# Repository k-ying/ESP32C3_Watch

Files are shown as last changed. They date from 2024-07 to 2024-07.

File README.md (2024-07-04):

# ESP32C3Watch
## 1. Brief/简介
The smartwatch made based on ESP32-C3(RISC-V MCU), which has heart rate, oximetry, temperature, fall detection and IOT Function. 

> 基于 ESP32-C3的智能手表（RISC-V MCU），具有心率、血氧饱和度、温度、跌倒检测和物联网功能。

The project stems from My Graduation Project in 2022, Since the time for secrecy has ended, I can open source its design and code.The project may be very old, some components and functions can not be used directly, need to be adjusted according to the latest library, please be aware of.

> 该项目源于2022年的毕业设计，因为已满足时间，所以开源其设计与代码。该项目可能比较旧了，有些组件和函数不能直接使用，需要根据最新的库进行调整，请悉知。

Here are the folder descriptions:
1. HardWare: used to store hardware related, circuit design and PCB design, using KiCAD for the design of the project; also contains 3D models and peripherals DataSheet.
2. Software: used to store the programme code of CMU master control, this project uses ESP-IDF (LVGL library) of VScode environment to build the project, the version may be very old.
3. Article: thesis and reference materials.
4. images: README.md needed images.

> 以下是文件夹说明：
> 1. HardWare：用于存放硬件相关，电路设计及PCB设计，使用KiCAD进行设计的工程；还包含3D模型及外设DataSheet。
> 2. Software：用于存放CMU主控的程序代码，该项目使用VScode环境的ESP-IDF(LVGL库)进行工程建立，版本可能很旧了。
> 3. Article：论文及参考资料。
> 4. images：README.md 需要的图片。

## 2. Architecture/架构：
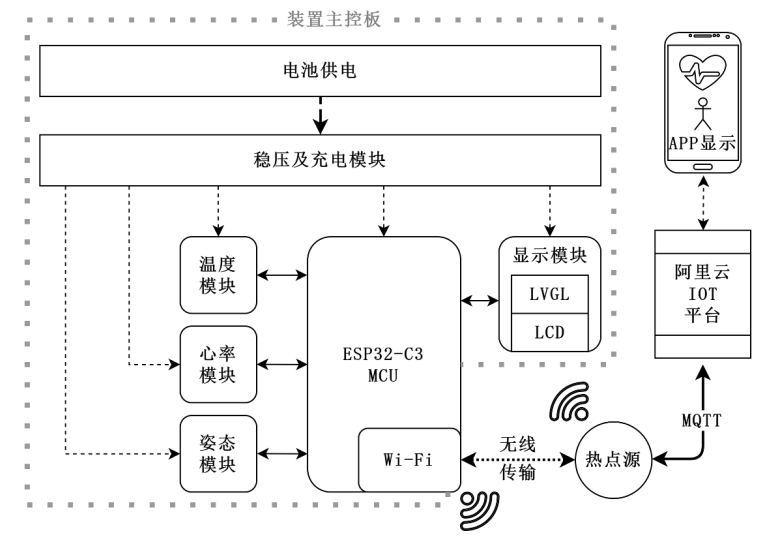
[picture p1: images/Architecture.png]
Architecture


In view of foreign chip design enterprises may take the technology monopoly, coupled with the COVID-19 has made people pay more attention to a healthy life. This topic designed a wearable human health monitoring device based on RISC-V architecture MCU, which can detect the wearer's heart rate, blood oxygen saturation, skin surface temperature, and exercise status in real-time. After scheme comparison, the ESP32-C3 series of Espressif Systems CO., LTD. was selected as the master chip. The MAX30102 sensor was used to obtain photoplethysmogram(PPG) signals, which can calculate heart rate and blood oxygen saturation(SpO2) data. MAX30205 was used to obtain real-time temperature, and MPU-6050 Inertial measurement unit(IMU) was used to obtain motion state data, so as to realize the functions of sedentary and falling reminder.

A GUI interface based on LVGL allows users to interact with the device and view data, ifconnected to a Wi-Fi hotspot, it will upload data to the AliCloud IOT server via MQTT. Through the AliCloud data visualization platform, users can view historical data and fall alarm information by using the supporting APP.

After finishing the design, the device defects were found and optimized through various 
functional tests. Finally, good stability of the device and accuracy of data was realized.

> 鉴于国外芯片设计企业可能采取的技术垄断，加之疫情让人们对健康生活更加重视，本课题设计了一款基于 RISC-V 架构 MCU 的穿戴式人体健康监测装置，可实时检测佩戴者的心率和血氧饱和度、皮肤表面温度以及运动状态等健康参数。经过方案比对，最终选择乐鑫科技的 ESP32-C3 系列作为主控芯片，使用 MAX30102 传感器获取光电容积脉搏波（PPG）并计算心率、血氧饱和度(SpO2)数据，通过 MAX30205 获取实时温度、MPU-6050 惯性测量单元(IMU)获取运动状态数据，从而实现久坐、跌倒提醒等功能。

> 用户可通过基于 LVGL 设计的 GUI 界面进行人机交互、数据查看，还可将装置连接至 Wi-Fi 热点，数据会通过 MQTT 协议上传至阿里云 IOT 服务器。借由阿里数据可视化平台，用户端可使用配套 APP 查看历史数据、跌倒警报信息等。

> 装置设计完成后，通过各项功能测试，发现存在设计缺陷并进行了改正及优化，最终实现了装置的稳定与数据的准确可靠。

## 3. Schematic/原理图
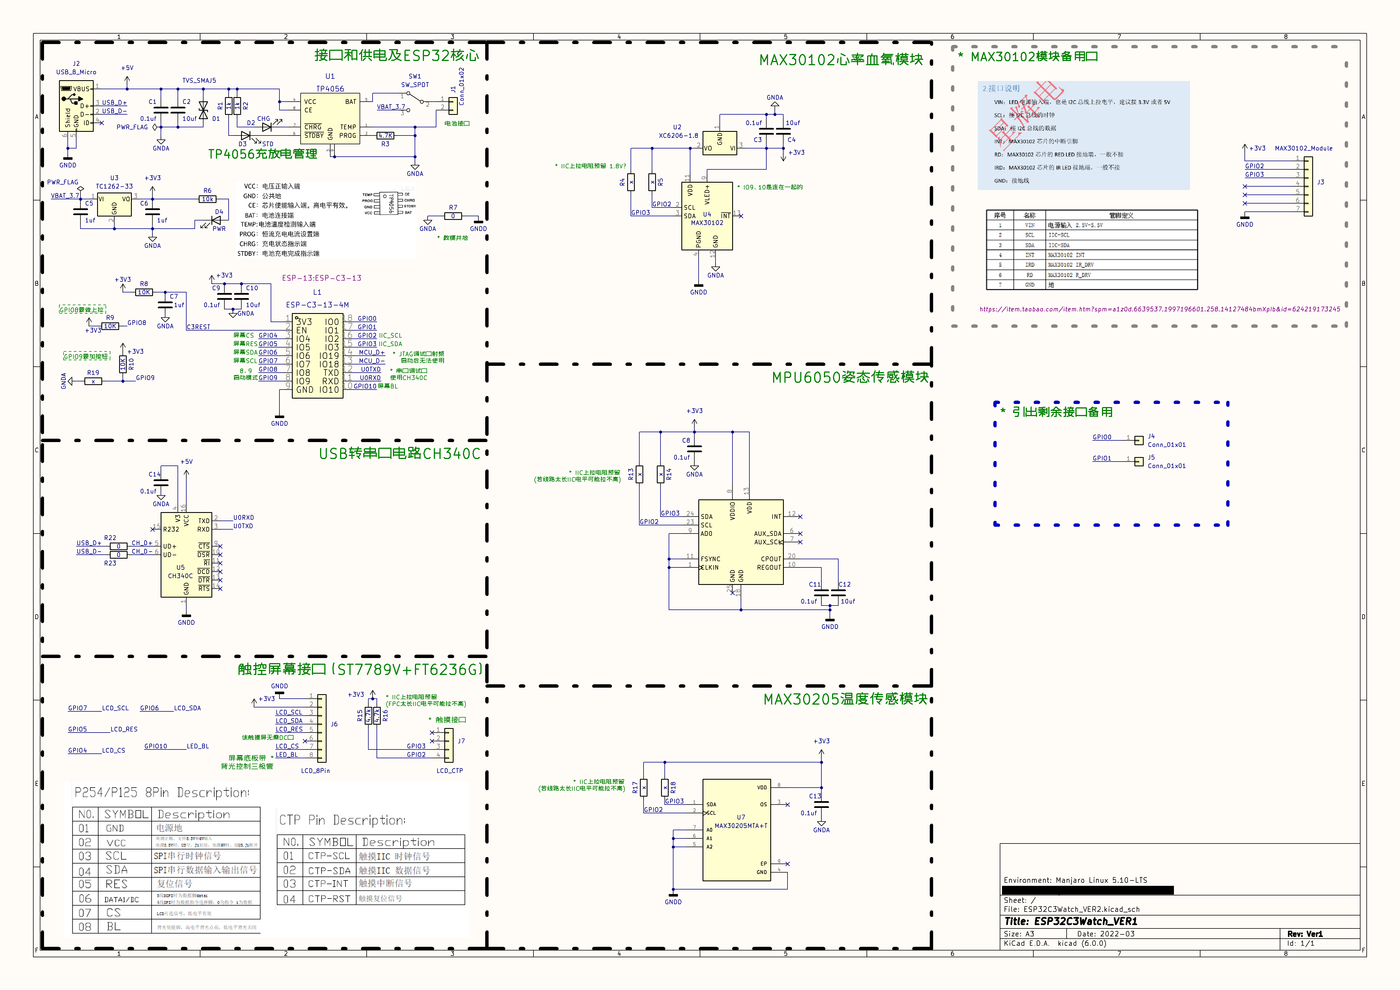
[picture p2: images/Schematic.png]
Schematic


For a detailed description, please see the Article/ESP32C3Watch_CN.pdf

> 详细的介绍请见文件 Article/ESP32C3Watch_CN.pdf

## 4. PCB

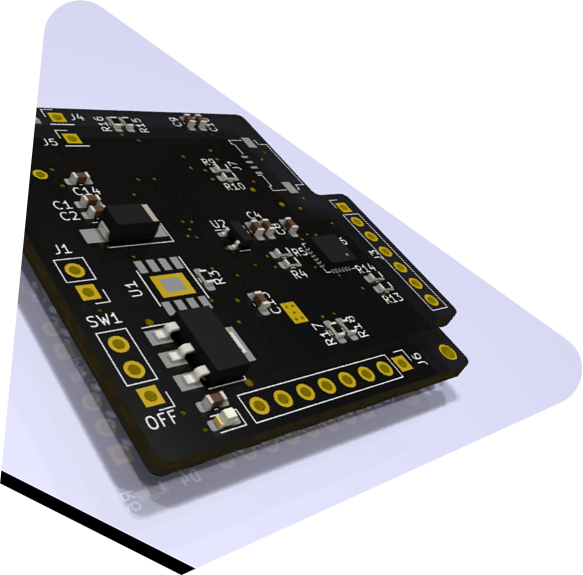
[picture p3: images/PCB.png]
PCB


The PCB is just used as a reference, it can actually be made better and smaller. For a detailed description, please see the Article/ESP32C3Watch_CN.pdf

> PCB只是作为一个参考，实际上它可以做得更好、更小巧。详细的介绍请见文件 Article/ESP32C3Watch_CN.pdf

## 5. Function/功能

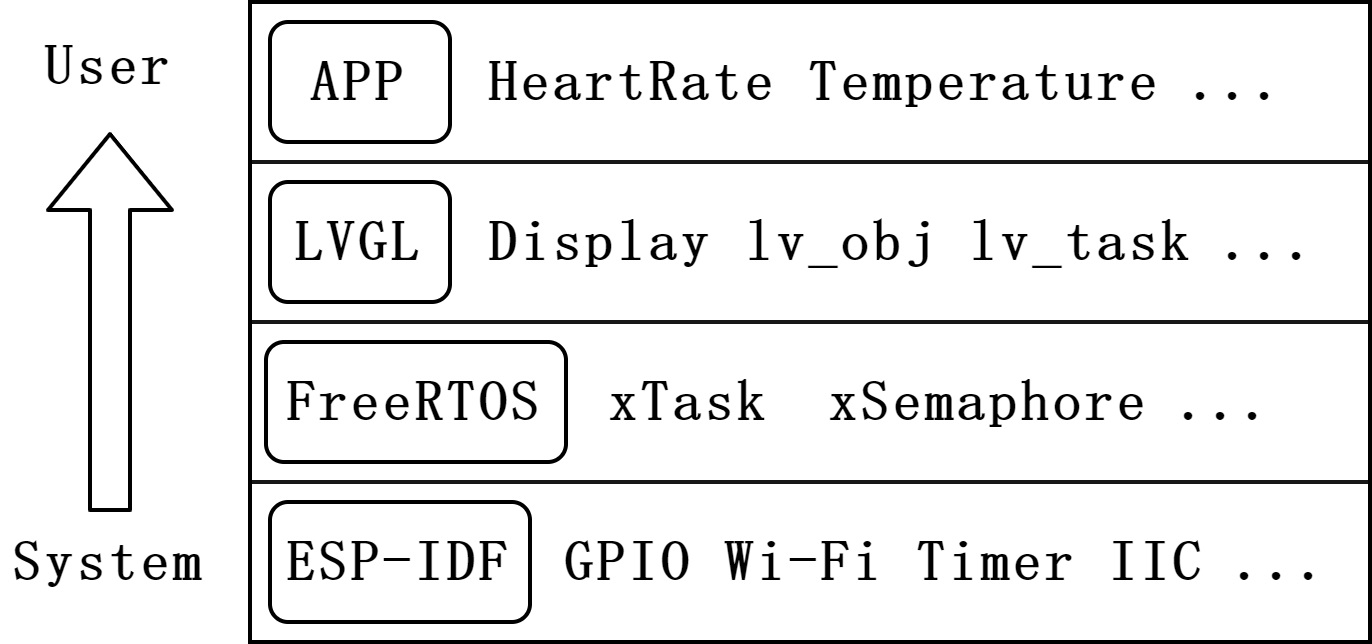
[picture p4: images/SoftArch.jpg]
SoftArch


For a detailed description, please see the Article/ESP32C3Watch_CN.pdf

> 详细的介绍请见文件 Article/ESP32C3Watch_CN.pdf

## 6. Display results/结果展示

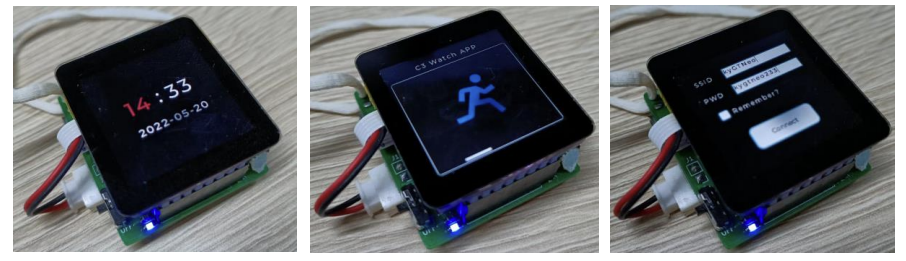
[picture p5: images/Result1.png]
Result1


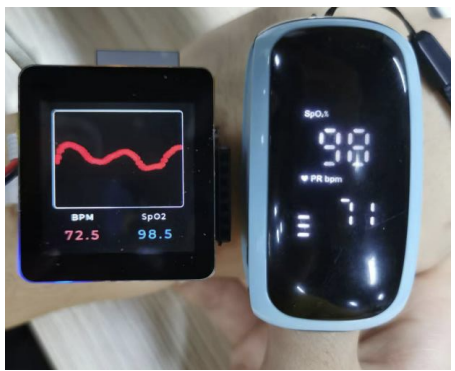
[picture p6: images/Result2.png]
Result2


For a detailed description, please see the Article/ESP32C3Watch_CN.pdf

> 详细的介绍请见文件 Article/ESP32C3Watch_CN.pdf

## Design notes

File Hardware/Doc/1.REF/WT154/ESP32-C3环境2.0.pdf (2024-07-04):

ESP32-C3 环境准备

1. Windows 环境搭建
a) 获取 ESP-IDFG
Windows 去官方网站下载一个 ESP-IDF 工具安装器 https://dl.espressif.com/dl/esp-idf/?idf=4.4 我这里使用的是离线安装器

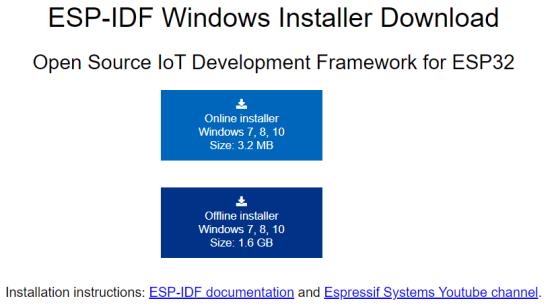
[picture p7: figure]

b) 安装

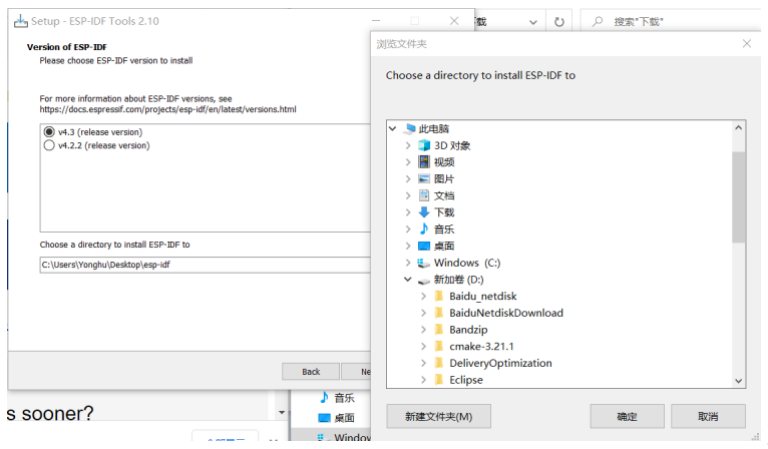
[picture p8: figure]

建议在 D 盘创建一个文件

夹去保存该 ESP-IDF ,因为后面需要把工程放在同一个目录下

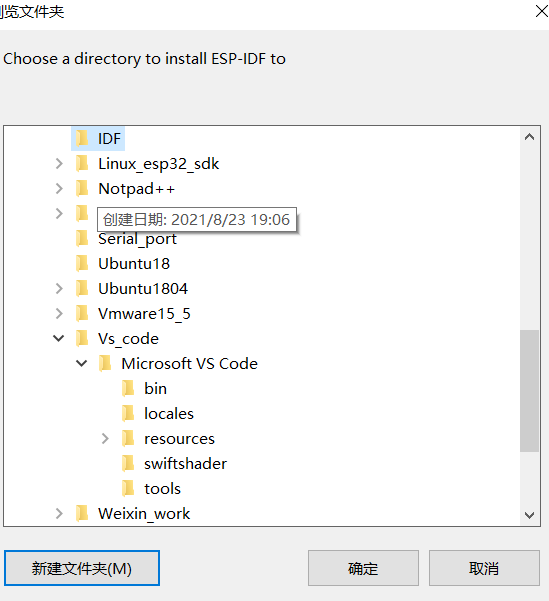
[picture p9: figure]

建立一个 IDF 文件夹去保存该 esp-idf 直接一直下一步到安装

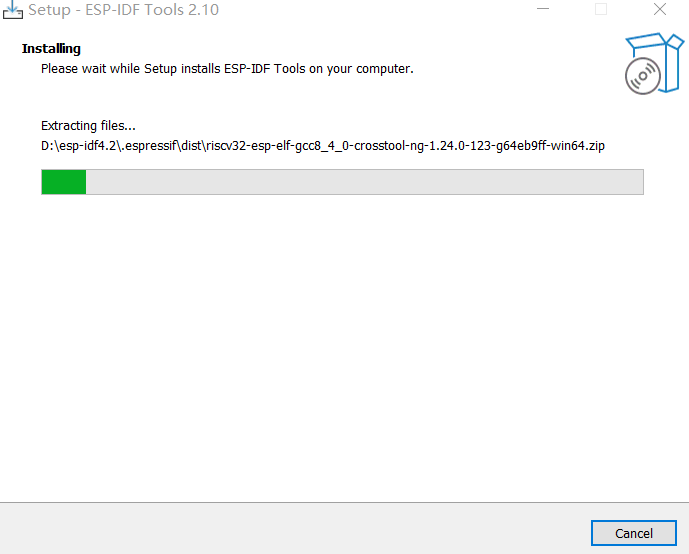
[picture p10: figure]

安装完成后会在桌面生成

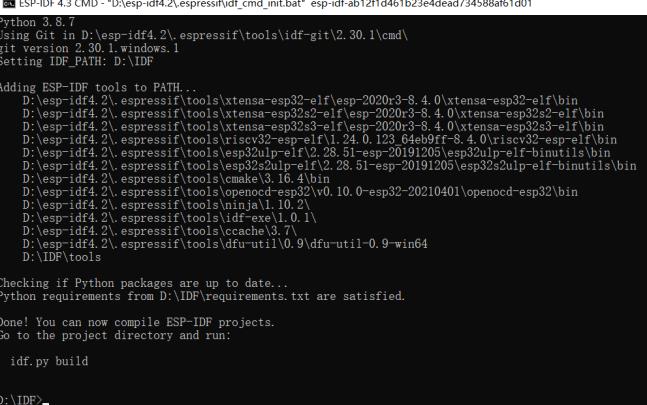
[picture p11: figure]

可以以管理身份运行( 但是不推荐), 如图已经可以使用 idf.py build 这样环境搭建完成,下面开始编译工程
2. 工程
a) 拷贝工程

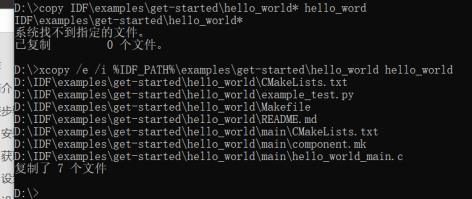
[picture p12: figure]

将 hello_word 复制到 d 盘下
xcopy /e /i %IDF_PATH%\examples\get-started\hello_world hello_world 这里安装没安装到 IDF 子目录下,所以选择直接在 d 盘选择一个文件夹作为工程目录 使用 dir 指令 查看当前所有文件

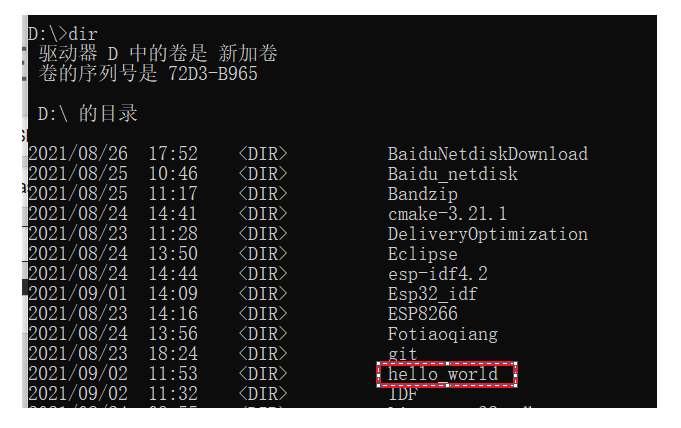
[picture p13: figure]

这个便是已经复制好的工程文件了
b) 设备连接

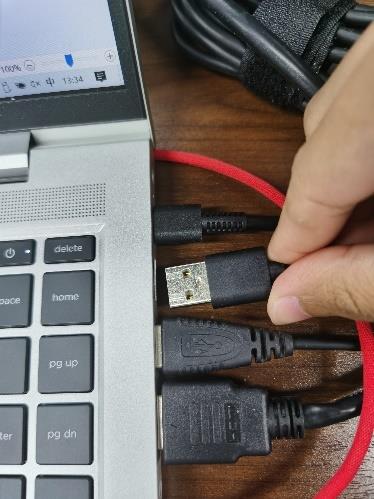
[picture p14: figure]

c) 设置目标芯片 :

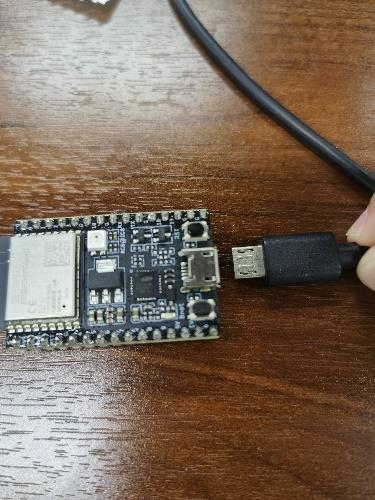
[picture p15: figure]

idf.py set-target esp32c3 设置目标芯片

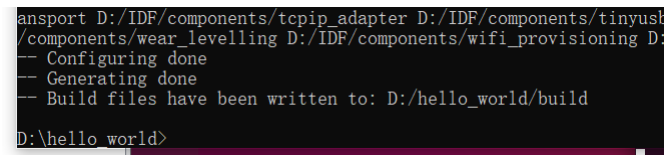
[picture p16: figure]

idf.py menuconfig 打开工程配置主窗口命令

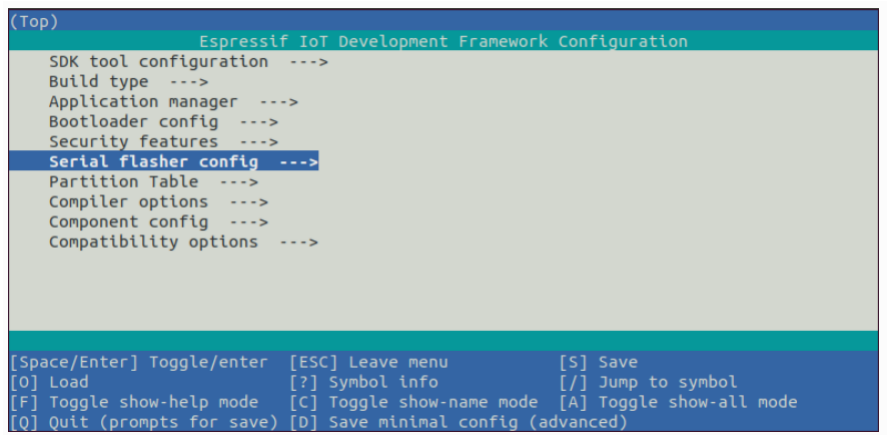
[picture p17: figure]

d) 编译工程
进入到已经克隆的文件 hello_world 编译命令 : idf.py build

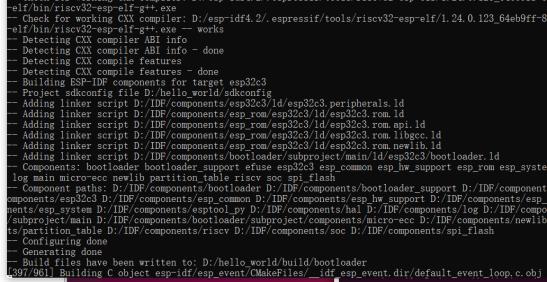
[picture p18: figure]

e) | 烧入到设备 idf.py -p port [ -b BAUD] | flash
-p port 表示需要指定的端口号 -b BAUD 可以不用写指的是波特率不写默认烧入波特率为 :
| 460800
f) 环境 打开设备管理器 找到
| 按下 windows 按键/鼠标单击左小角

键盘输入设备管理器

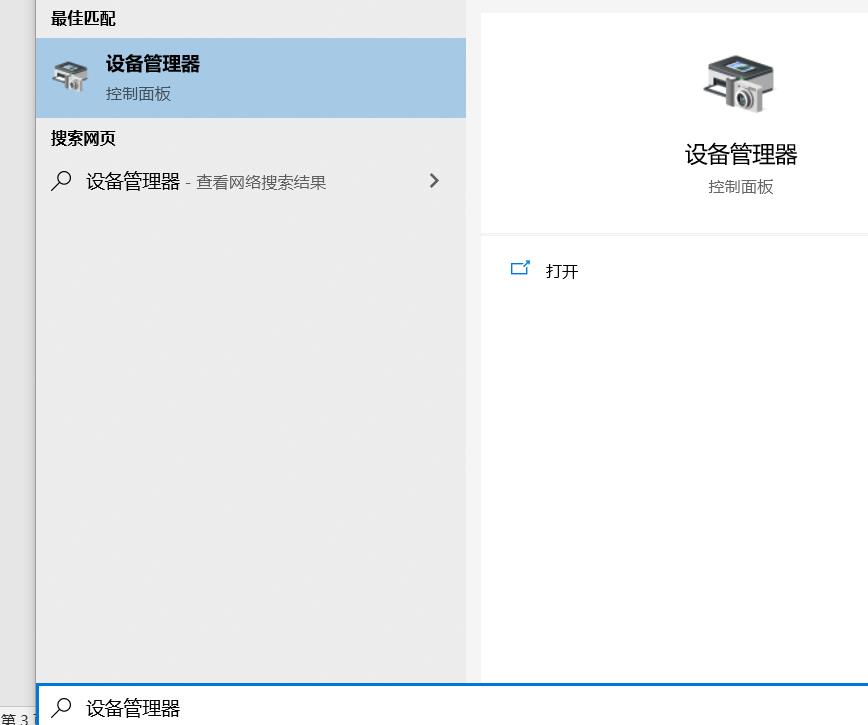
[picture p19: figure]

找到 COM 和 LPT 选项

当 COM 口未连接设备不会有该选项
idf.py -p (PORT) monitor
这个 PORT 即端口号, 如上则是 COM3 命令 : idf.py -p COM3 monitor 也可以使用软件 : 串口调试工具

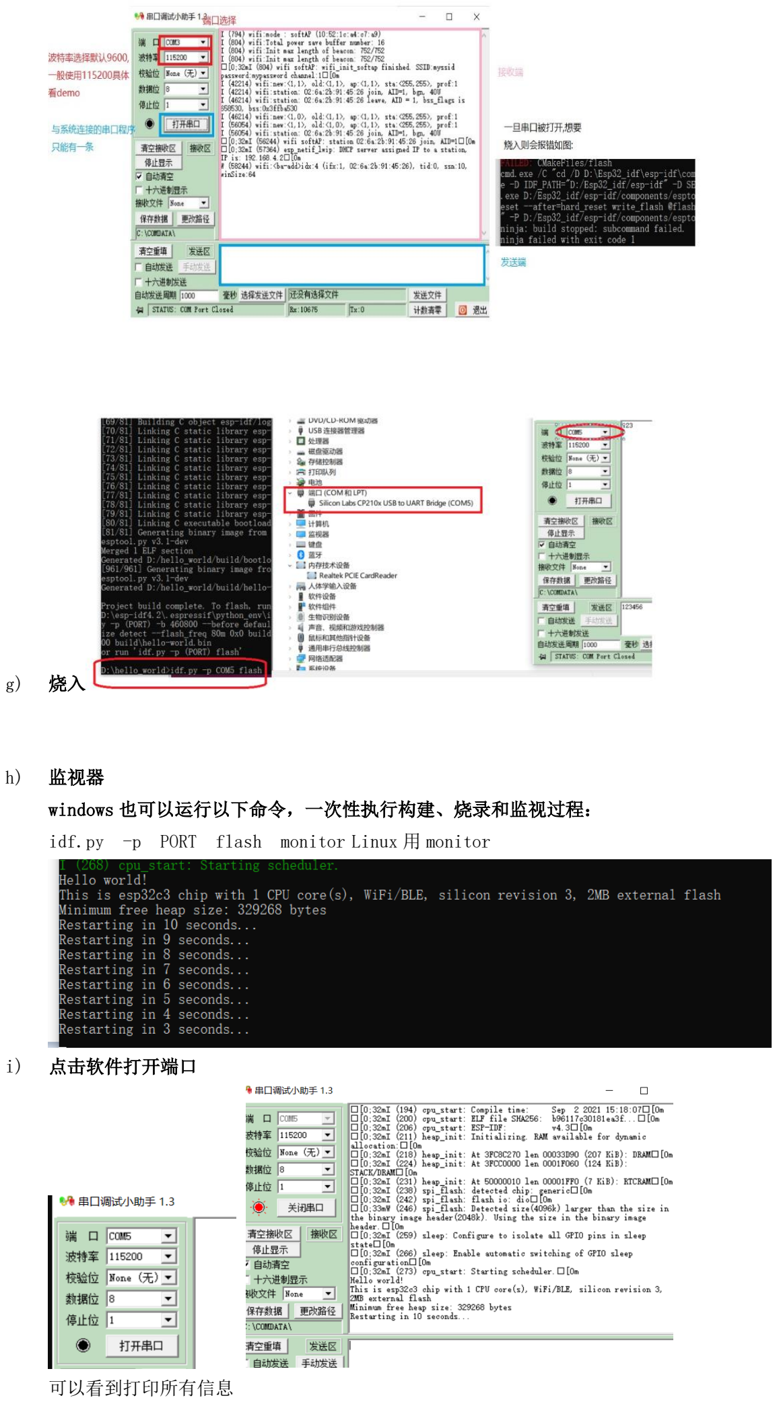
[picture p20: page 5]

g) 烧入
h) 监视器
windows 也可以运行以下命令，一次性执行构建、烧录和监视过程： idf.py -p PORT flash monitor Linux 用 monitor
i) 点击软件打开端口

可以看到打印所有信息

### Ubuntu 下的环境安装

1. 下载 cmake 及 python3 环境 和 ninja-build git
sudo apt-get install git wget flex bison gperf python3 python3-pip python3-setuptools cmake ninja-build ccache libffi-dev libssl-dev dfu-util libusb-1.0-0
编译的软件包

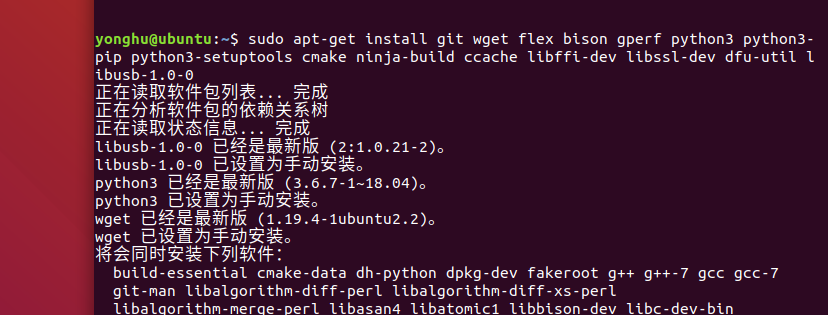
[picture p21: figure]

键入 Y

我们装好了工具, 现在安装 esp-idf 先 cd 到你想安装到的路径我这里选择桌面

2. 在当前路径下创建文件夹 esp 这样可以看见桌面生成了一个文件夹 cd ./esp 转到刚刚创建的文件夹
git clone --recursive https://github.com/espressif/esp-idf.git 克隆文件到当面路径下,也就是刚刚创建的文件夹 esp

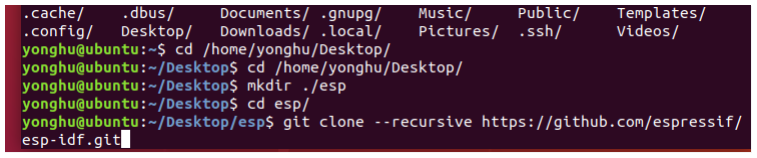
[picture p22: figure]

3. Linux 则需要 先 cd ~/esp/esp-idf 即刚刚下载的路径 这里的 ~ 表示 家目录 /home/yonghu
然后 : ./install.sh esp32c3

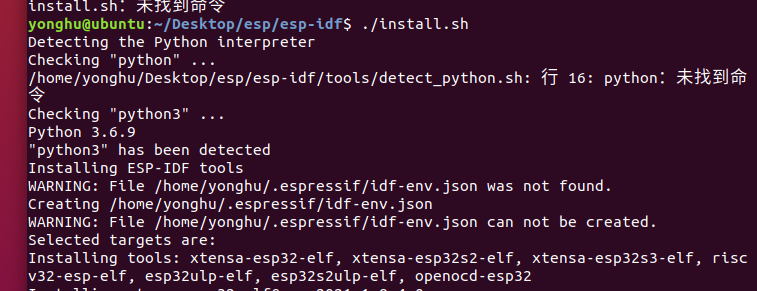
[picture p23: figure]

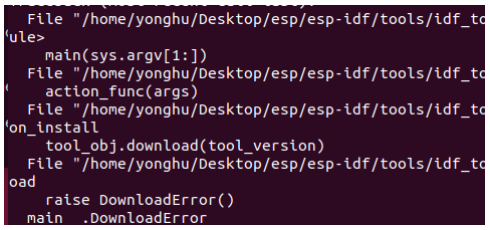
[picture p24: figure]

报错解决办法
输入 git submodule update --init --recursive 更新 需要多次尝试直到完全克隆

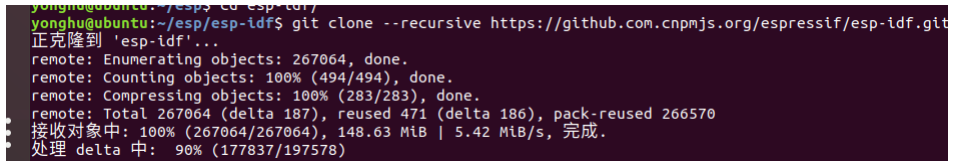
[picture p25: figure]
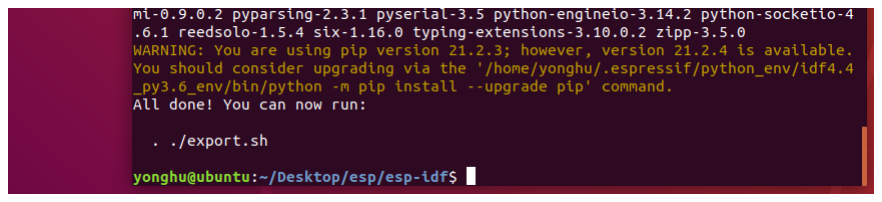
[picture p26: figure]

可能遇见找不到文件
解决办法 : find /usr/include -name "io.h"

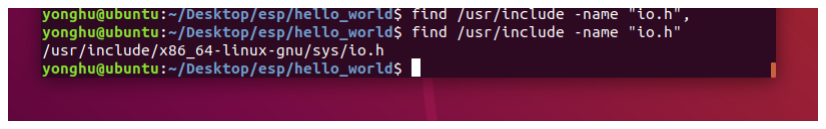
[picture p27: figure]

可以看到 sys 目录下有
/usr/include 下没有，但是在/usr/include/sys 下有，我把 io.h 复制到了/usr/include 下，就行了 由于上面出错可能导致该命令未生效
接着 :. ./export.sh esp32c3 ( esp32c3 打不打无所谓)
4. 写入环境
. $HOME/esp/esp-idf/export.sh
此外，如果您希望在当下命令提示符窗口使用 ESP-IDF，请使用下方代码： 复制并粘贴以下命令到 shell 配置文件中（.profile， .bashrc， .zprofile 等)
alias get_idf='. $HOME/esp/esp-idf/export.sh'
通过重启终端窗口或运行 source [path to profile]，如 source ~/.bashrc 来刷新配置文件。
5. 拷贝目录
cp ./esp-idf/examples/get-started/hello_world/ ./ -r

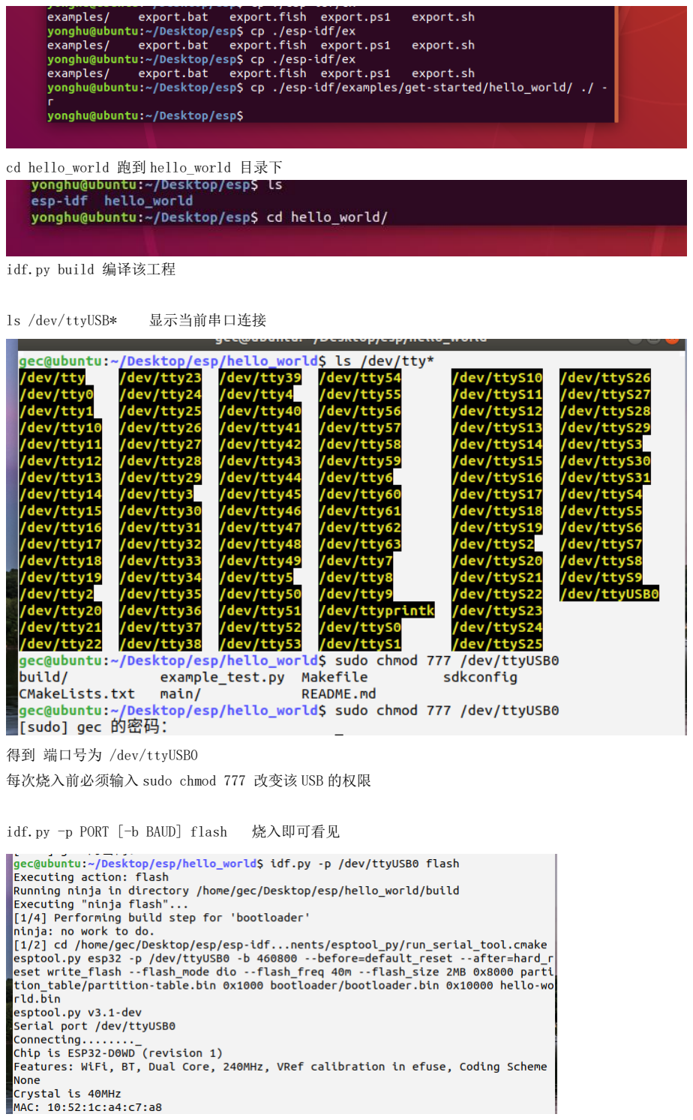
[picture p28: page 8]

cd hello_world 跑到 hello_world 目录下

idf.py build 编译该工程

ls /dev/ttyUSB* 显示当前串口连接

得到 端口号为 /dev/ttyUSB0
每次烧入前必须输入 sudo chmod 777 改变该 USB 的权限

idf.py -p PORT [-b BAUD] flash 烧入即可看见

6. 观察串口打印信息
idf.py -p (PORT) monitor
这个 PORT 即端口号, 如上则是 /dev/ttyUSB0 命令 : idf.py -p /dev/ttyUSB0 monitor

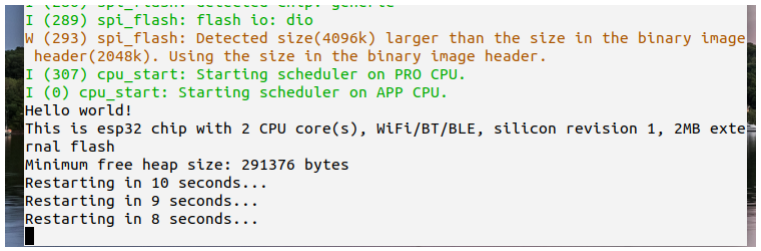
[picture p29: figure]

就可以看见所有打印信息

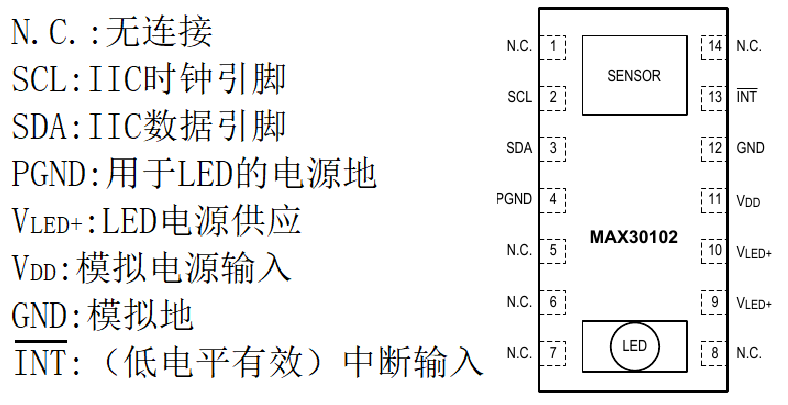
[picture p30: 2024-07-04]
Hardware/Doc/2.DATASHEET/max30102.png

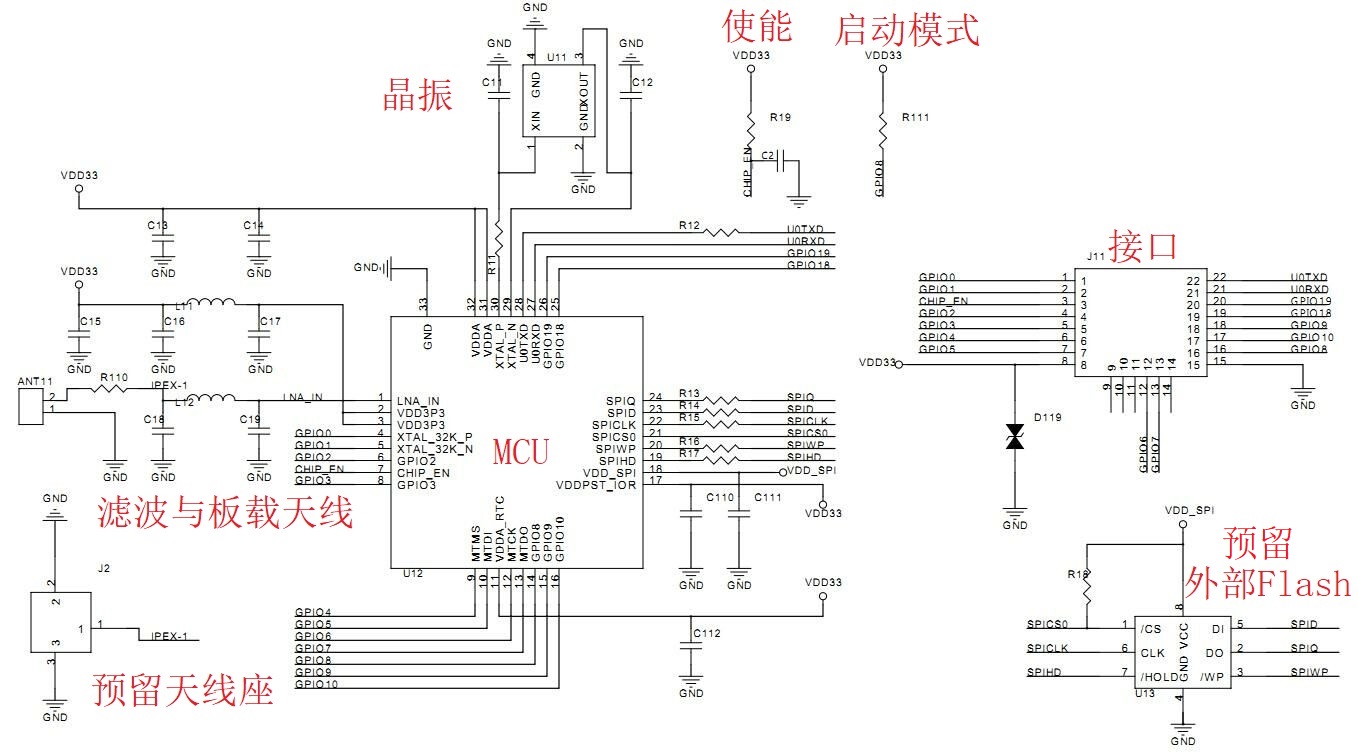
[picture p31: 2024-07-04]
Hardware/Doc/1.REF/esp-c3-13_specification-00000010.jpg

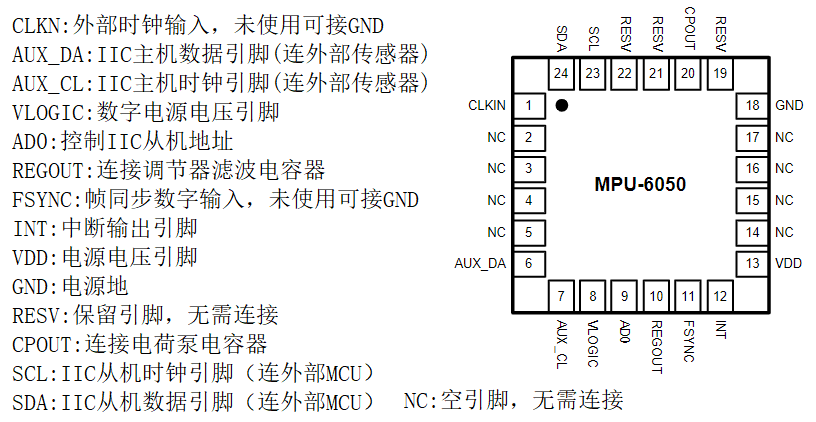
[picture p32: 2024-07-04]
Hardware/Doc/2.DATASHEET/mpu6050.png

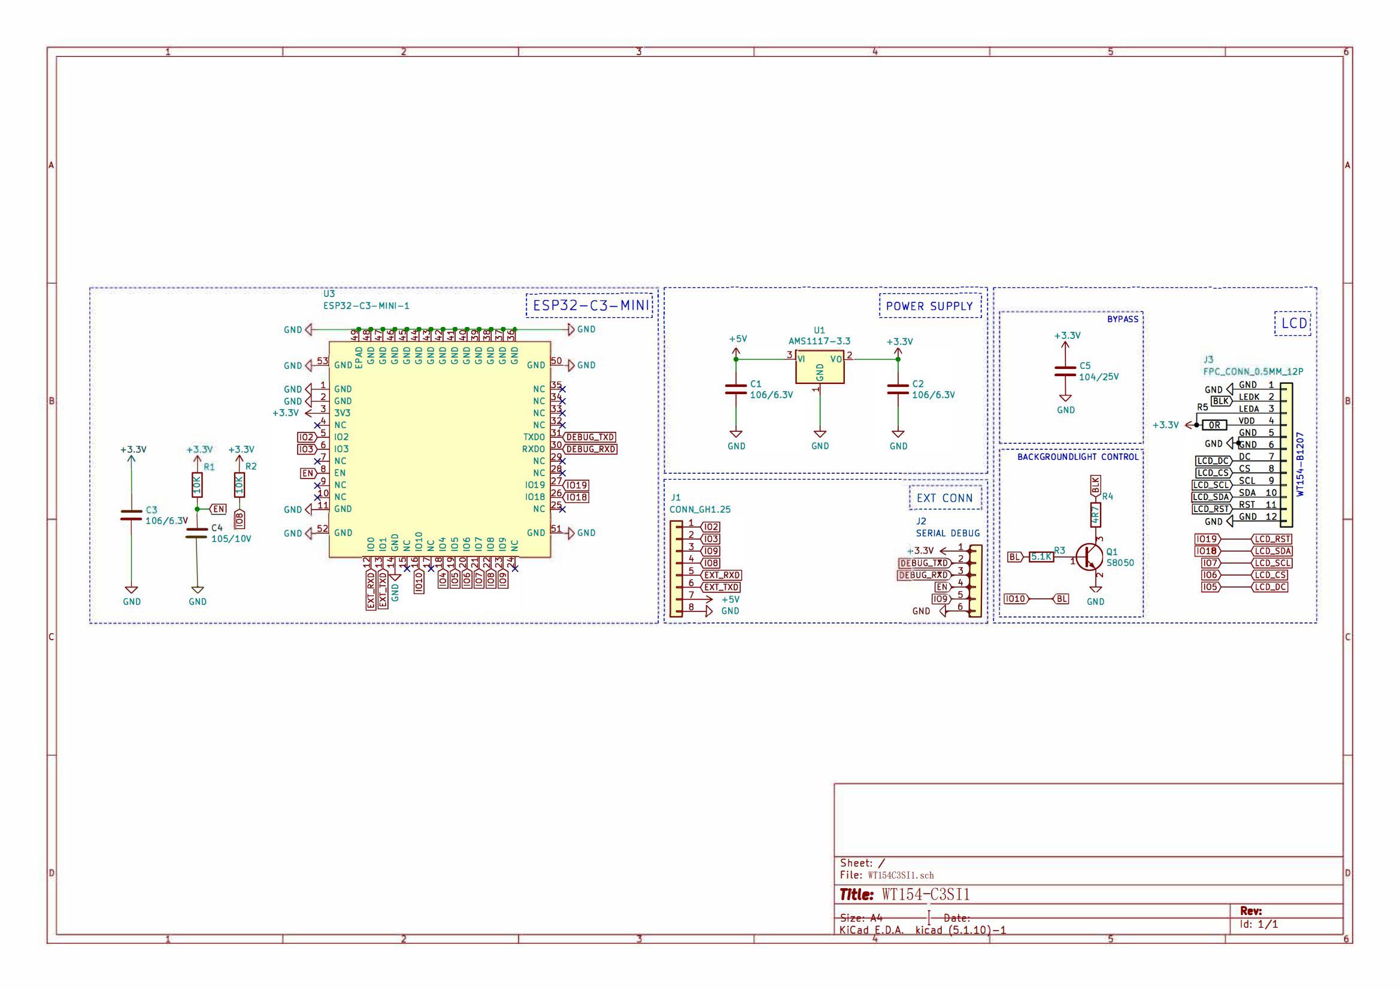
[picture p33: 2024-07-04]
Hardware/Doc/1.REF/SCH_WT154-C3SI1.jpg

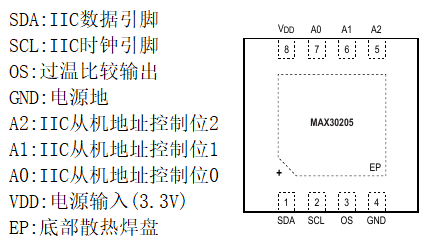
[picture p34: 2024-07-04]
Hardware/Doc/2.DATASHEET/max30205.png

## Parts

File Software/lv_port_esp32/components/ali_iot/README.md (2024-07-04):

将组件内容放入到项目下就可以将组件加入到项目中
//下面的几个宏用于定义设备的阿里云身份认证信息：ProductKey、ProductSecret、DeviceName、DeviceSecret
//在实际产品开发中，设备的身份认证信息应该是设备厂商将其加密后存放于设备Flash中或者某个文件中，
//设备上电时将其读出后使用
```
#define LIGHT_PRODUCT_KEY "xx"
#define LIGHT_PRODUCT_SECRET "xxx"
#define LIGHT_DEVICE_NAME "light"
#define LIGHT_DEVICE_SECRET "xxxx"

在启动mqtt协议时
iotx_dev_meta_info_t meta_info;
iotx_sign_mqtt_t sign_mqtt;

memset(&meta_info, 0, sizeof(iotx_dev_meta_info_t));
//下面的代码是将上面静态定义的设备身份信息赋值给meta_info
memcpy(meta_info.product_key, LIGHT_PRODUCT_KEY, strlen(EXAMPLE_PRODUCT_KEY));
memcpy(meta_info.product_secret, LIGHT_PRODUCT_SECRET, strlen(EXAMPLE_PRODUCT_SECRET));
memcpy(meta_info.device_name, LIGHT_DEVICE_NAME, strlen(EXAMPLE_DEVICE_NAME));
memcpy(meta_info.device_secret, LIGHT_DEVICE_SECRET, strlen(EXAMPLE_DEVICE_SECRET));

//调用签名函数，生成MQTT连接时需要的各种数据
IOT_Sign_MQTT(IOTX_CLOUD_REGION_SHANGHAI, &meta_info, &sign_mqtt);

esp_mqtt_client_config_t mqtt_cfg = {
    .host = sign_mqtt.hostname,
    .port = 1883,
    .password = sign_mqtt.password,
    .client_id = sign_mqtt.clientid,
    .username = sign_mqtt.username,
    .event_handle = mqtt_event_handler,
};
```

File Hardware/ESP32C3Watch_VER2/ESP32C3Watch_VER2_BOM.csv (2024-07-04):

Comment | Description | Designator | Footprint | LibRef | Pins | Quantity | PartNumber | url
0.1uf | desc | C1,C3,C8,C9,C13,C14, | C_0603_1608Metric_Pad1.08x0.95mm_HandSolder | libref | 2 | 6
10uf | desc | C2,C4,C10, | C_0603_1608Metric_Pad1.08x0.95mm_HandSolder | libref | 2 | 3
1uf | desc | C6, | C_0603_1608Metric_Pad1.08x0.95mm_HandSolder | libref | 2 | 1
TVS_SMAJ5 | desc | D1, | D_SMA_Handsoldering | libref | 2 | 1
PWR | desc | D4, | LED_0603_1608Metric_Pad1.05x0.95mm_HandSolder | libref | 2 | 1
LCD_CTP | desc | J7, | Molex_200528-0040_1x04-1MP_P1.00mm_Horizontal | libref | 6 | 1
4.7K | desc | R3, | R_0603_1608Metric_Pad0.98x0.95mm_HandSolder | libref | 2 | 1
x | desc | R4,R5,R13,R14,R17,R18, | R_0603_1608Metric_Pad0.98x0.95mm_HandSolder | libref | 2 | 6
0 | desc | R7, | R_0603_1608Metric_Pad0.98x0.95mm_HandSolder | libref | 2 | 1
10K | desc | R9,R10, | R_0603_1608Metric_Pad0.98x0.95mm_HandSolder | libref | 2 | 2
4.7k | desc | R15,R16, | R_0603_1608Metric_Pad0.98x0.95mm_HandSolder | libref | 2 | 2
TP4056 | desc | U1, | Diodes_SO-8EP | libref | 9 | 1
XC6206-1.8 | desc | U2, | SOT-23 | libref | 3 | 1
TC1262-33 | desc | U3, | SOT-223-3_TabPin2 | libref | 4 | 1
MPU-6050 | desc | U6, | InvenSense_QFN-24_4x4mm_P0.5mm | libref | 25 | 1
1uf | desc | C5,C7, | C_0603_1608Metric_Pad1.08x0.95mm_HandSolder | libref | 2 | 2
0.1uf | desc | C11, | C_0603_1608Metric_Pad1.08x0.95mm_HandSolder | libref | 2 | 1
10uf | desc | C12, | C_0603_1608Metric_Pad1.08x0.95mm_HandSolder | libref | 2 | 1
CHG | desc | D2, | LED_0603_1608Metric_Pad1.05x0.95mm_HandSolder | libref | 2 | 1
STD | desc | D3, | LED_0603_1608Metric_Pad1.05x0.95mm_HandSolder | libref | 2 | 1
ESP-C3-13-4M | desc | L1, | ESP-C3-13 | libref | 18 | 1
1k | desc | R1,R2, | R_0603_1608Metric_Pad0.98x0.95mm_HandSolder | libref | 2 | 2
10k | desc | R6, | R_0603_1608Metric_Pad0.98x0.95mm_HandSolder | libref | 2 | 1
10K | desc | R8, | R_0603_1608Metric_Pad0.98x0.95mm_HandSolder | libref | 2 | 1
x | desc | R19, | R_0603_1608Metric_Pad0.98x0.95mm_HandSolder | libref | 2 | 1
0 | desc | R22,R23, | R_0603_1608Metric_Pad0.98x0.95mm_HandSolder | libref | 2 | 2
MAX30102 | desc | U4, | Maxim_OLGA-14_3.3x5.6mm_P0.8mm | libref | 14 | 1
CH340C | desc | U5, | SOIC-16_3.9x9.9mm_P1.27mm | libref | 16 | 1
MAX30205MTA+T | desc | U7, | SON65P300X300X80-9N | libref | 9 | 1
Through Hole Items
 | desc | ,, |  | libref | 1 | 2
Conn_01x02 | desc | J1, | PinHeader_1x02_P2.54mm_Vertical | libref | 2 | 1
MAX30102_Module | desc | J3, | PinHeader_1x07_P2.54mm_Vertical | libref | 7 | 1
Conn_01x01 | desc | J4,J5, | PinHeader_1x01_P2.54mm_Vertical | libref | 1 | 2
LCD_8Pin | desc | J6, | PinHeader_1x08_P2.54mm_Vertical | libref | 8 | 1
SW_SPDT | desc | SW1, | PinHeader_1x03_P2.54mm_Vertical | libref | 3 | 1
USB_B_Micro | desc | J2, | USB_Micro-B_Molex-105017-0001 | libref | 13 | 1

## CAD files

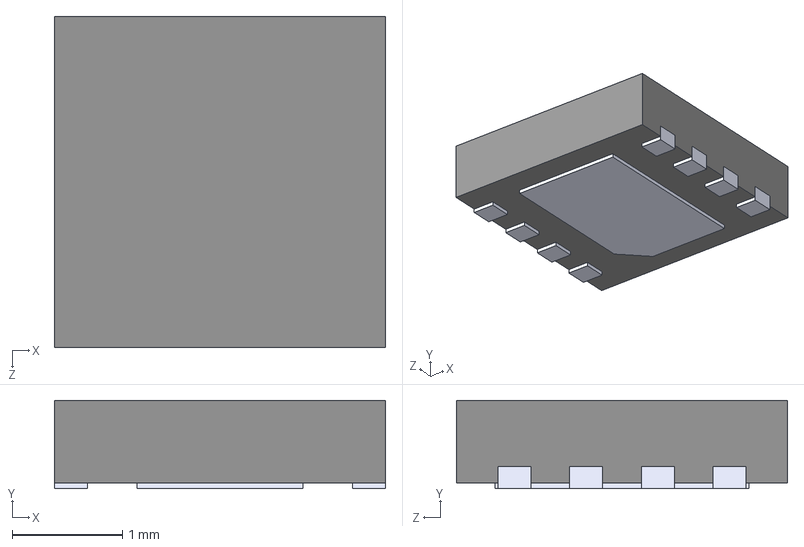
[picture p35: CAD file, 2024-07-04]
Hardware/ESP32C3Watch_VER2/ProjSym/3dmodels/MAX30205MTA_T.step
3.00 x 0.8 x 3.00 mm

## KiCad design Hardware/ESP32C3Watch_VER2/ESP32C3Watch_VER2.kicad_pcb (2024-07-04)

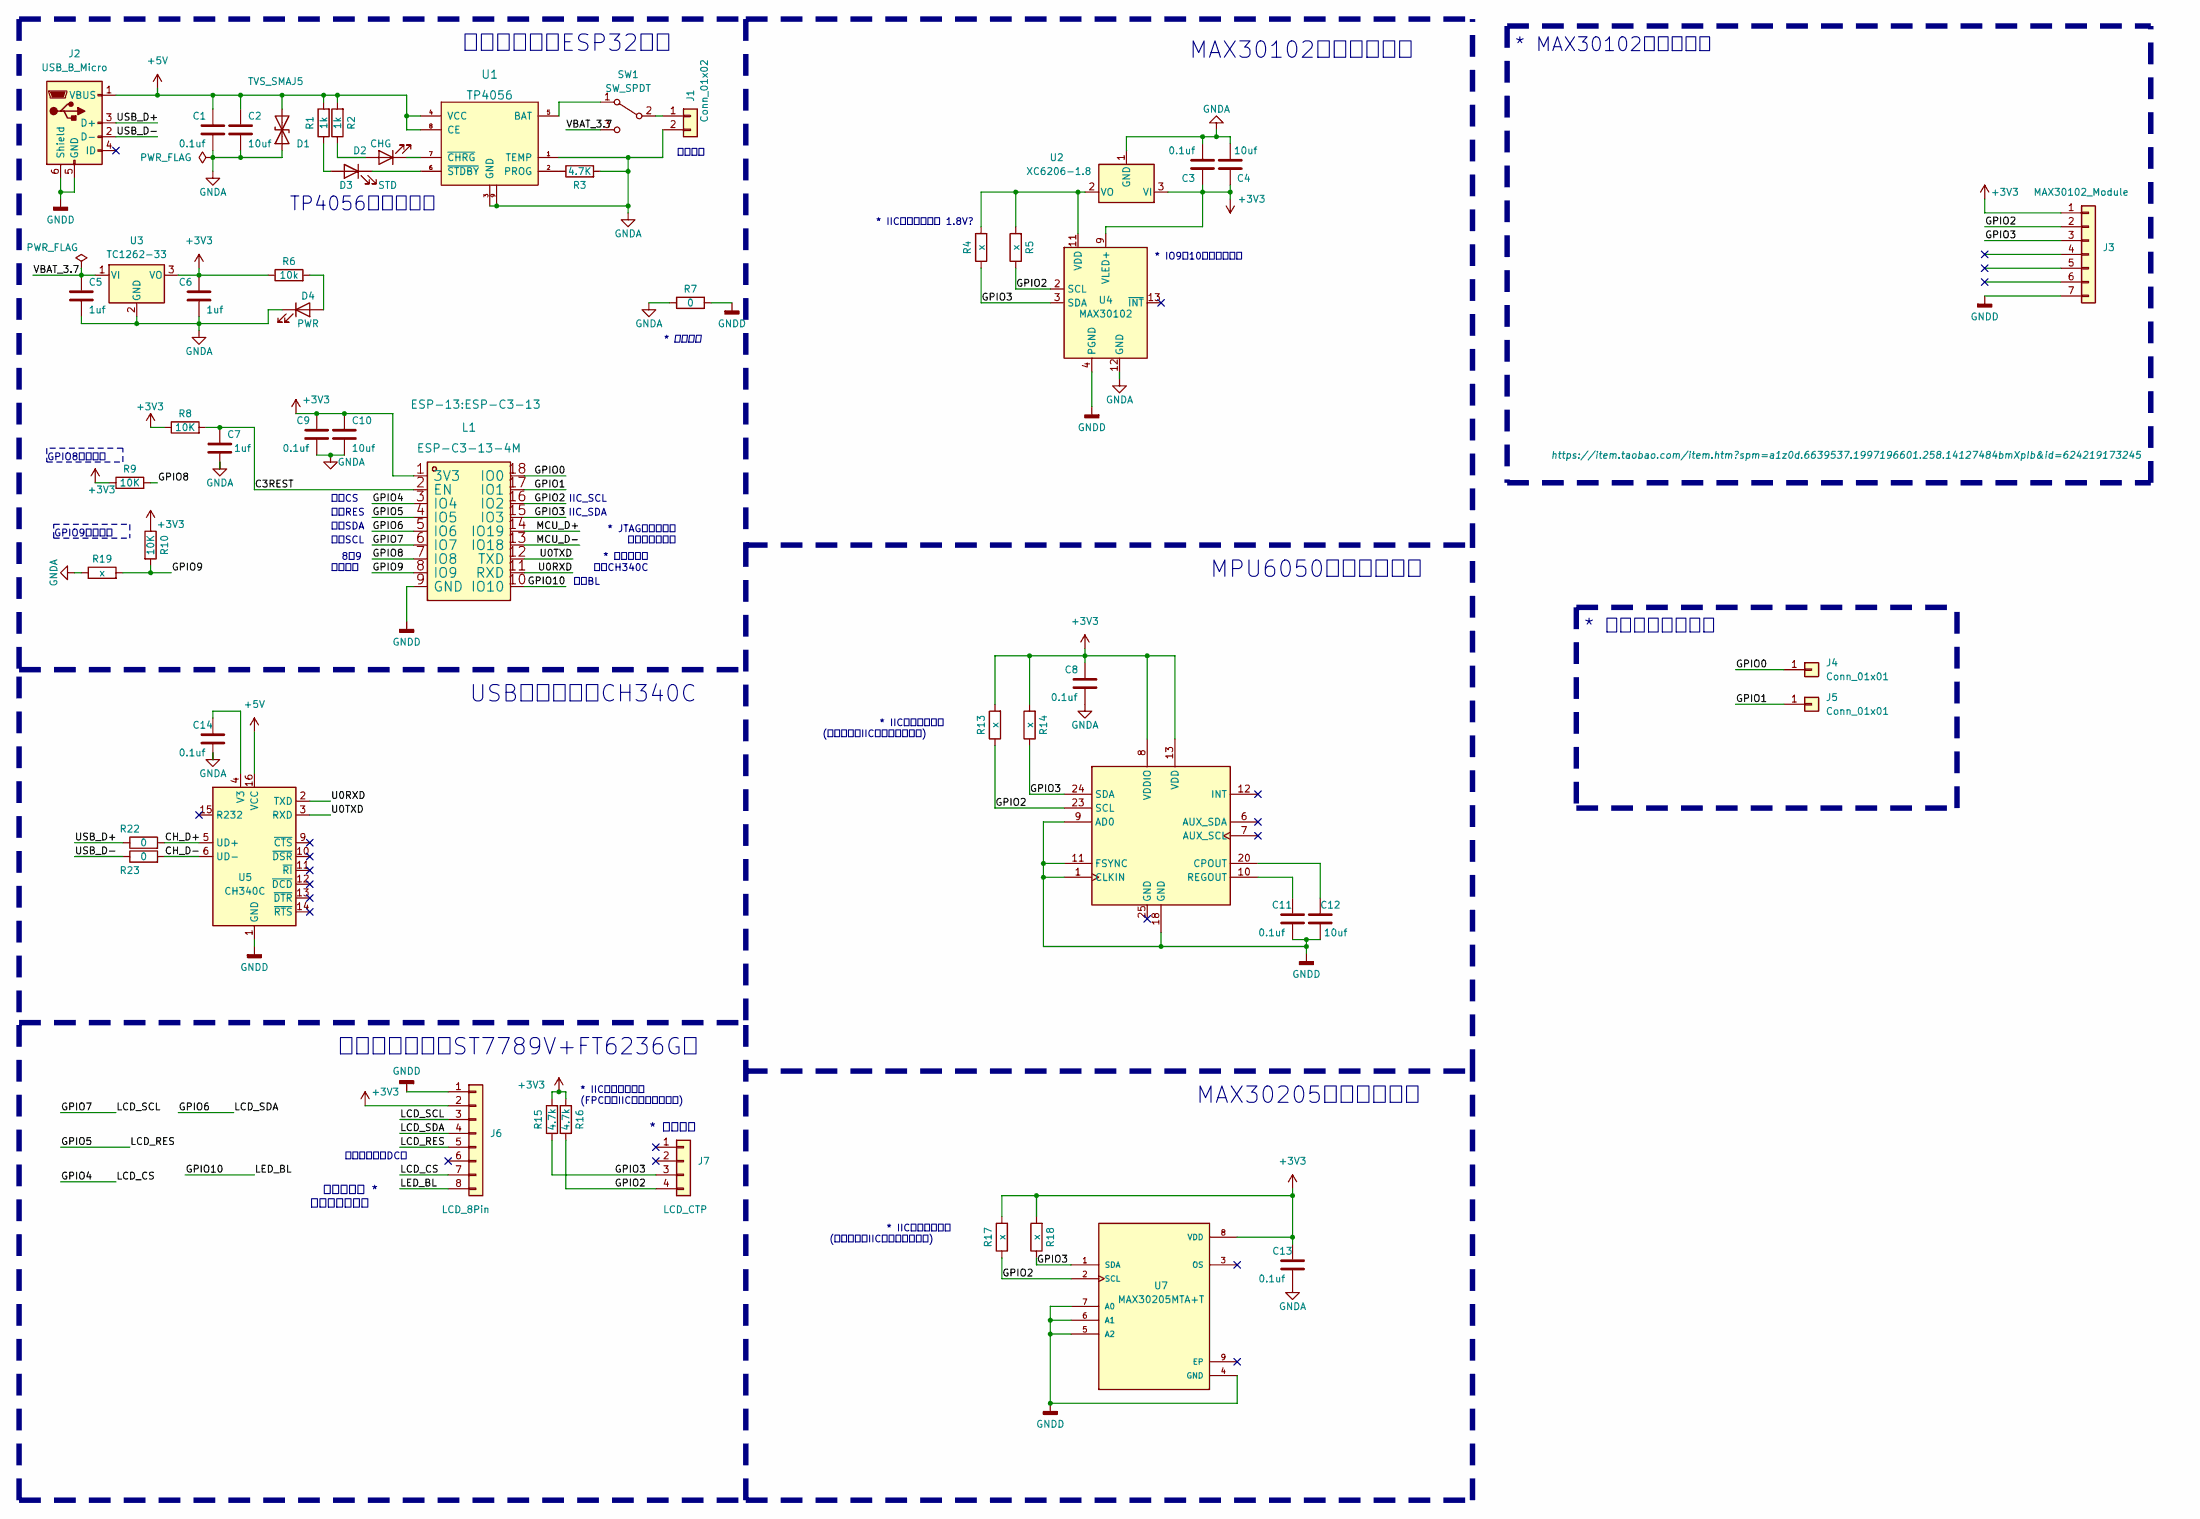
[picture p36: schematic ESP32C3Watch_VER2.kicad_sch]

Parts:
C1, C3, C8, C9, C11, C13, C14: 0.1uf; C_0603_1608Metric_Pad1.08x0.95mm_HandSolder
C2, C4, C10, C12: 10uf; C_0603_1608Metric_Pad1.08x0.95mm_HandSolder
C5, C6, C7: 1uf; C_0603_1608Metric_Pad1.08x0.95mm_HandSolder
D1: TVS_SMAJ5; D_SMA_Handsoldering
D2: CHG; LED_0603_1608Metric_Pad1.05x0.95mm_HandSolder
D3: STD; LED_0603_1608Metric_Pad1.05x0.95mm_HandSolder
D4: PWR; LED_0603_1608Metric_Pad1.05x0.95mm_HandSolder
J1: Conn_01x02; PinHeader_1x02_P2.54mm_Vertical
J2: USB_B_Micro; USB_Micro-B_Molex-105017-0001
J3: MAX30102_Module; PinHeader_1x07_P2.54mm_Vertical
J4: Conn_01x01; PinHeader_1x01_P1.00mm_Vertical
J5: Conn_01x01; PinHeader_1x01_P2.54mm_Vertical
J6: LCD_8Pin; PinHeader_1x08_P2.54mm_Vertical
J7: LCD_CTP; Molex_200528-0040_1x04-1MP_P1.00mm_Horizontal
L1: ESP-C3-13-4M; ESP-C3-13
R1, R2: 1k; R_0603_1608Metric_Pad0.98x0.95mm_HandSolder
R3: 4.7K; R_0603_1608Metric_Pad0.98x0.95mm_HandSolder
R4, R5, R13, R14, R17, R18, R19: x; R_0603_1608Metric_Pad0.98x0.95mm_HandSolder
R6: 10k; R_0603_1608Metric_Pad0.98x0.95mm_HandSolder
R7, R22, R23: 0; R_0603_1608Metric_Pad0.98x0.95mm_HandSolder
R8, R9, R10: 10K; R_0603_1608Metric_Pad0.98x0.95mm_HandSolder
R15, R16: 4.7k; R_0603_1608Metric_Pad0.98x0.95mm_HandSolder
SW1: SW_SPDT; SW_CuK_OS102011MA1QN1_SPDT_Angled
U1: TP4056; Diodes_SO-8EP
U2: XC6206-1.8; SOT-23
U3: TC1262-33; SOT-223-3_TabPin2
U4: MAX30102; Maxim_OLGA-14_3.3x5.6mm_P0.8mm
U5: CH340C; SOIC-16_3.9x9.9mm_P1.27mm
U6: MPU-6050; InvenSense_QFN-24_4x4mm_P0.5mm
U7: MAX30205MTA+T; SON65P300X300X80-9N

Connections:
+3V3: C3.1, C4.1, C6.1, C8.1, C9.1, C10.1, C13.1, J3.1, J6.2, L1.1 (3V3), R6.1, R8.1, R9.1, R10.1, R13.2, R14.2, R15.2, R16.2, R17.2, R18.2, U2.3 (VI), U3.3 (VO), U4.9 (VLED+), U4.10 (VLED+), U6.8 (VDDIO), U6.13 (VDD), U7.8 (VDD)
+5V: C1.1, C2.1, D1.2 (A2), J2.1 (VBUS), R1.2, R2.2, U1.4 (VCC), U1.8 (CE), U5.16 (VCC)
/C3REST: C7.1, L1.2 (EN), R8.2
/CH_D+: R22.2, U5.5 (UD+)
/CH_D-: R23.2, U5.6 (UD-)
/GPIO0: J4.1, L1.18 (IO0)
/GPIO1: J5.1, L1.17 (IO1)
/GPIO2: J3.2, J7.4, L1.16 (IO2), R5.1, R13.1, R16.1, R17.1, U4.2 (SCL), U6.23 (SCL), U7.2 (SCL)
/GPIO3: J3.3, J7.3, L1.15 (IO3), R4.1, R14.1, R15.1, R18.1, U4.3 (SDA), U6.24 (SDA), U7.1 (SDA)
/GPIO4: J6.7, L1.3 (IO4)
/GPIO5: J6.5, L1.4 (IO5)
/GPIO6: J6.4, L1.5 (IO6)
/GPIO7: J6.3, L1.6 (IO7)
/GPIO8: L1.7 (IO8), R9.2
/GPIO9: L1.8 (IO9), R10.2, R19.2
/GPIO10: J6.8, L1.10 (IO10)
/MCU_D+: L1.14 (IO19)
/MCU_D-: L1.13 (IO18)
/U0RXD: L1.11 (RXD), U5.2 (TXD)
/U0TXD: L1.12 (TXD), U5.3 (RXD)
/USB_D+: J2.3 (D+), R22.1
/USB_D-: J2.2 (D-), R23.1
/VBAT_3.7: C5.1, SW1.3 (C), U3.1 (VI)
GNDA: C1.2, C2.2, C3.2, C4.2, C5.2, C6.2, C7.2, C8.2, C9.2, C10.2, C13.2, C14.2, D1.1 (A1), D4.1 (K), J1.2, R3.2, R7.1, R19.1, U1.1 (TEMP), U1.3 (GND), U1.9, U2.1 (GND), U3.2 (GND), U4.12 (GND)
GNDD: C11.2, C12.2, J2.5 (GND), J2.6 (Shield), J3.7, J6.1, L1.9 (GND), R7.2, U4.4 (PGND), U5.1 (GND), U6.1 (CLKIN), U6.9 (AD0), U6.11 (FSYNC), U6.18 (GND), U7.4 (GND), U7.5 (A2), U7.6 (A1), U7.7 (A0)
unnamed: C11.1, U6.10 (REGOUT)
unnamed: C12.1, U6.20 (CPOUT)
unnamed: C14.1, U5.4 (V3)
unnamed: D2.1 (K), U1.7 (~CHRG)
unnamed: D2.2 (A), R2.1
unnamed: D3.1 (K), U1.6 (~STDBY)
unnamed: D3.2 (A), R1.1
unnamed: D4.2 (A), R6.2
unnamed: J1.1, SW1.2 (B)
unnamed: R3.1, U1.2 (PROG)
unnamed: R4.2, R5.2, U2.2 (VO), U4.11 (VDD)
unnamed: SW1.1 (A), U1.5 (BAT)

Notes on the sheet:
MAX30205温度传感模块
* IO9、10是连在一起的
屏幕CS
屏幕BL
* MAX30102模块备用口
GPIO9要加按钮
MAX30102心率血氧模块
IIC_SDA
* IIC上拉电阻预留 (若线路太长IIC电平可能拉不高)
8、9 启动模式
屏幕SDA
触控屏幕接口（ST7789V+FT6236G）
MPU6050姿态传感模块
屏幕SCL
接口和供电及ESP32核心
屏幕RES
* JTAG调试口射频 启动后无法使用
* 引出剩余接口备用
* IIC上拉电阻预留 (FPC太长IIC电平可能拉不高)
* IIC上拉电阻预留 1.8V?
* 触摸接口
电池接口
该触摸屏无需DC口
TP4056充放电管理
GPIO8要做上拉
* 串口调试口 使用CH340C
屏幕底板带 * 背光控制三极管
* 数模共地
USB转串口电路CH340C
IIC_SCL

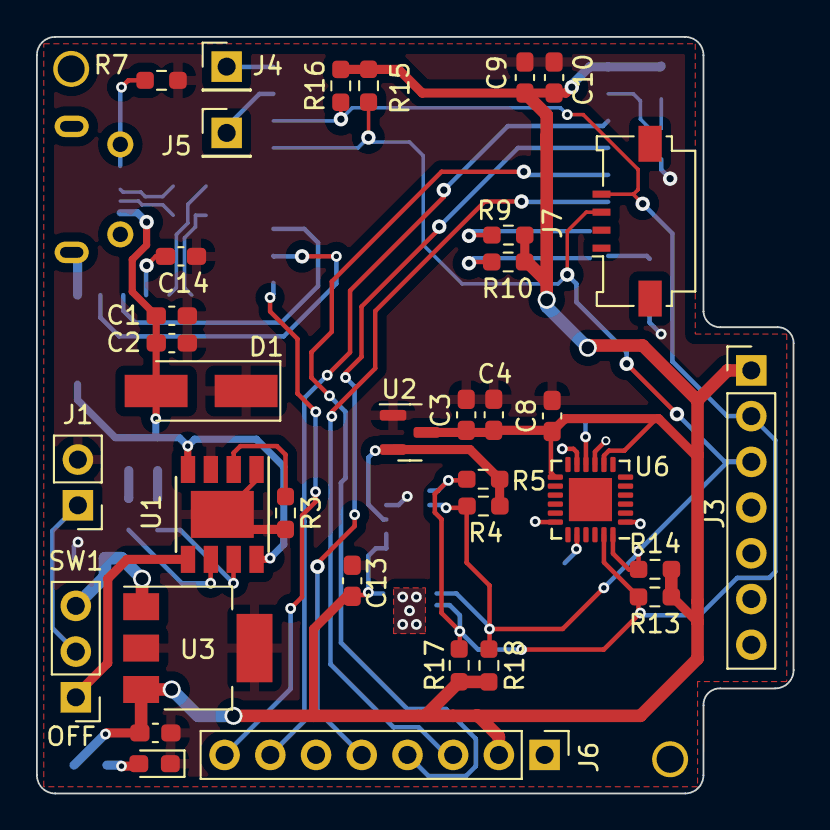
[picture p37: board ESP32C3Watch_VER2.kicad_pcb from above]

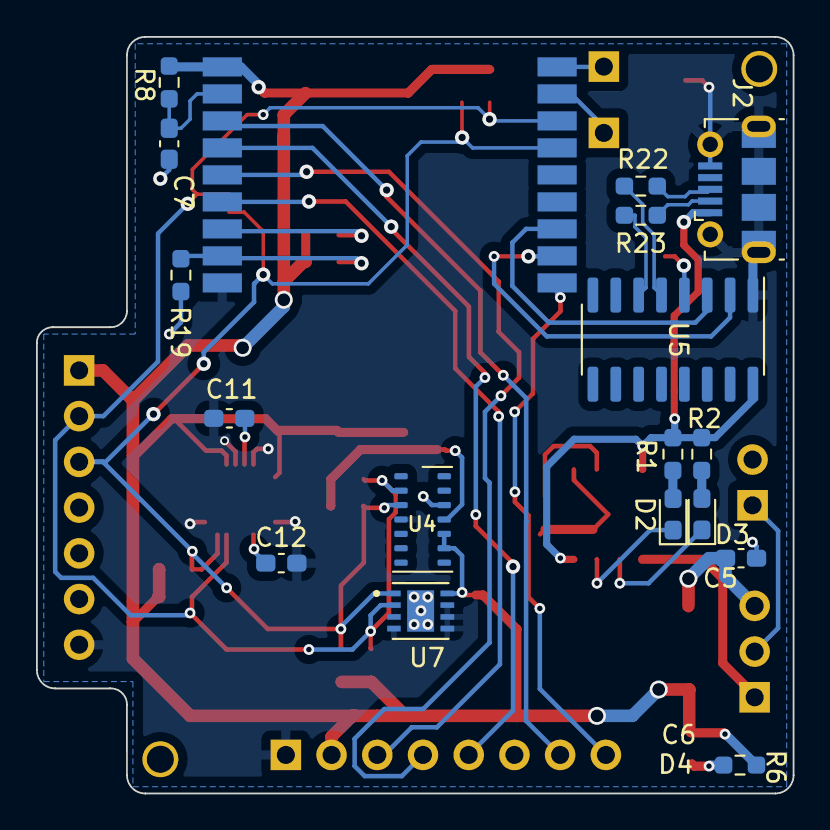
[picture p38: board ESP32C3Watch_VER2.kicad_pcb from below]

Board: 2 copper layers, 42.0 x 42.0 mm, 53 parts (18 on the bottom side), 35 nets.

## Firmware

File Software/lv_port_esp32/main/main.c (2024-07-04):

/* LVGL Example project
 *
 * Basic project to test LVGL on ESP32 based projects.
 *
 * This example code is in the Public Domain (or CC0 licensed, at your option.)
 *
 * Unless required by applicable law or agreed to in writing, this
 * software is distributed on an "AS IS" BASIS, WITHOUT WARRANTIES OR
 * CONDITIONS OF ANY KIND, either express or implied.
 */
#include <stdbool.h>
#include <stdio.h>
#include <stdlib.h>
#include <string.h>

#include "freertos/FreeRTOS.h"
#include "freertos/task.h"
#include "esp_freertos_hooks.h"
#include "freertos/semphr.h"
#include "esp_system.h"
#include "driver/gpio.h"

/* Littlevgl specific */
#ifdef LV_LVGL_H_INCLUDE_SIMPLE
#include "lvgl.h"
#else
#include "lvgl/lvgl.h"
//#include "components/lvgl/lvgl.h"
#endif
/* USER Need */
#include "lvgl_helpers.h"
#include "generated/gui_guider.h"
#include "generated/events_init.h"
#include "generated/custom/custom.h"
#include "MAX30205.h"
#include "max30102-registers.h"
#include "MPU6050.h"
#include "inv_mpu.h"
#include "inv_mpu_dmp_motion_driver.h"
#include "max30102.h"
#include "userwifi.h"
/****************** VAR *********************/
lv_ui guider_ui;
bool scrloading = false,Fallen=false,people_flag=false,sleep_flag=false;
uint8_t time_sec=0,time_min=0,time_hour=0,time_sync_flag=0;
char time_day[11];
float temp_value = 0,stepDis=0,stepF=0;
unsigned long step_count = 0;
max30102_config_t max30102 = {};
max30102_data_t result = {};
extern lv_chart_series_t * APPtoHR_chart_HeartBeep_0;
int HR_TIM_CNT=8000;
int16_t ax=0,ay=0,az=0;
/****************** VAR *********************/

#ifndef CONFIG_LV_TFT_DISPLAY_MONOCHROME
    #if defined CONFIG_LV_USE_DEMO_WIDGETS
        #include "lv_examples/src/lv_demo_widgets/lv_demo_widgets.h"
    #elif defined CONFIG_LV_USE_DEMO_KEYPAD_AND_ENCODER
        #include "lv_examples/src/lv_demo_keypad_encoder/lv_demo_keypad_encoder.h"
    #elif defined CONFIG_LV_USE_DEMO_BENCHMARK
        #include "lv_examples/src/lv_demo_benchmark/lv_demo_benchmark.h"
    #elif defined CONFIG_LV_USE_DEMO_STRESS
        #include "lv_examples/src/lv_demo_stress/lv_demo_stress.h"
    #else
        #error "No demo application selected."
    #endif
#endif

/*********************
 *      DEFINES
 *********************/
#define TAG "demo"
#define LV_TICK_PERIOD_MS 1

/**********************
 *  STATIC PROTOTYPES
 **********************/
static void lv_tick_task(void *arg);
// static void sec_tick_task(void *arg);
// static void Xms_tick_task(void *arg);
void lv_sec_task(lv_task_t * sec_task);
void lv_xms_task(lv_task_t * xms_task);
static void guiTask(void *pvParameter);
// static void create_demo_application(void);
void memory_print(void);
/**********************
 *   APPLICATION MAIN
 **********************/
void app_main() {
    /* If you want to use a task to create the graphic, you NEED to create a Pinned task
     * Otherwise there can be problem such as memory corruption and so on.
     * NOTE: When not using Wi-Fi nor Bluetooth you can pin the guiTask to core 0 */
    gpio_pad_select_gpio(ST7789_BCKL);                // BCKL OFF when boot
    gpio_set_direction(ST7789_BCKL, GPIO_MODE_OUTPUT);// 
    gpio_set_level(ST7789_BCKL, 0);                   // 
    xTaskCreatePinnedToCore(guiTask, "gui", 4096*13, NULL, 0, NULL, 0);
}

/* Creates a semaphore to handle concurrent call to lvgl stuff
 * If you wish to call *any* lvgl function from other threads/tasks
 * you should lock on the very same semaphore! */
SemaphoreHandle_t xGuiSemaphore;

static void guiTask(void *pvParameter) {

    (void) pvParameter;
    xGuiSemaphore = xSemaphoreCreateMutex();

    lv_init();

    /* Initialize SPI or I2C bus used by the drivers */
    lvgl_driver_init();

    lv_color_t* buf1 = heap_caps_malloc(DISP_BUF_SIZE * sizeof(lv_color_t), MALLOC_CAP_DMA);
    assert(buf1 != NULL);

    /* Use double buffered when not working with monochrome displays */
#ifndef CONFIG_LV_TFT_DISPLAY_MONOCHROME
    lv_color_t* buf2 = heap_caps_malloc(DISP_BUF_SIZE * sizeof(lv_color_t), MALLOC_CAP_DMA);
    assert(buf2 != NULL);
#else
    static lv_color_t *buf2 = NULL;
#endif

    static lv_disp_buf_t disp_buf;

    uint32_t size_in_px = DISP_BUF_SIZE;

#if defined CONFIG_LV_TFT_DISPLAY_CONTROLLER_IL3820         \
    || defined CONFIG_LV_TFT_DISPLAY_CONTROLLER_JD79653A    \
    || defined CONFIG_LV_TFT_DISPLAY_CONTROLLER_UC8151D     \
    || defined CONFIG_LV_TFT_DISPLAY_CONTROLLER_SSD1306

    /* Actual size in pixels, not bytes. */
    size_in_px *= 8;
#endif

    /* Initialize the working buffer depending on the selected display.
     * NOTE: buf2 == NULL when using monochrome displays. */
    lv_disp_buf_init(&disp_buf, buf1, buf2, size_in_px);

    lv_disp_drv_t disp_drv;
    lv_disp_drv_init(&disp_drv);
    disp_drv.flush_cb = disp_driver_flush;

    /* When using a monochrome display we need to register the callbacks:
     * - rounder_cb
     * - set_px_cb */
#ifdef CONFIG_LV_TFT_DISPLAY_MONOCHROME
    disp_drv.rounder_cb = disp_driver_rounder;
    disp_drv.set_px_cb = disp_driver_set_px;
#endif

    disp_drv.buffer = &disp_buf;
    lv_disp_drv_register(&disp_drv);

    /* Register an input device when enabled on the menuconfig */
#if CONFIG_LV_TOUCH_CONTROLLER != TOUCH_CONTROLLER_NONE
    lv_indev_drv_t indev_drv;
    lv_indev_drv_init(&indev_drv);
    indev_drv.read_cb = touch_driver_read;
    indev_drv.type = LV_INDEV_TYPE_POINTER;
    lv_indev_drv_register(&indev_drv);
#endif
    
    /* Create and start a periodic timer interrupt to call lv_tick_inc */
    esp_timer_handle_t periodic_timer;//periodic_sec_timer,periodic_Xms_timer;
    const esp_timer_create_args_t periodic_timer_args = {
        .callback = &lv_tick_task,
        .name = "periodic_gui"
    };
    ESP_ERROR_CHECK(esp_timer_create(&periodic_timer_args, &periodic_timer));
    ESP_ERROR_CHECK(esp_timer_start_periodic(periodic_timer, LV_TICK_PERIOD_MS * 1000));//定时器单位us，此操作1ms调用一次lv_tick_inc(1)

    /*********************************** Create LVGL application ************************************/
    //create_demo_application();
	setup_ui(&guider_ui);
    // events_init(&guider_ui);
    // custom_init(&guider_ui);
    /*************************************** Sensor Init ********************************************/
    int ret = MAX30205_Init();
    if(ret==ESP_OK){
        printf("MAX30205_Init Successful!\n");
    }else{
        printf("MAX30205_Init Error!\n");
    }
    ret = mpu_dmp_init();
    if(ret==0){
        printf("MPU6050_Init Successful!\n");
    }else{
        printf("MPU6050_Init Error!\n");
    }
    ESP_ERROR_CHECK(max30102_init( &max30102, I2C_NUM_0,
               MAX30102_DEFAULT_OPERATING_MODE,
               MAX30102_DEFAULT_SAMPLING_RATE,
               MAX30102_DEFAULT_LED_PULSE_WIDTH,
               MAX30102_DEFAULT_IR_LED_CURRENT,
               MAX30102_DEFAULT_START_RED_LED_CURRENT,
               MAX30102_DEFAULT_MEAN_FILTER_SIZE,
               MAX30102_DEFAULT_PULSE_BPM_SAMPLE_SIZE,
               MAX30102_DEFAULT_ADC_RANGE, 
               MAX30102_DEFAULT_SAMPLE_AVERAGING,
               MAX30102_DEFAULT_ROLL_OVER,
               MAX30102_DEFAULT_ALMOST_FULL,
               false ));
    gpio_pad_select_gpio(ST7789_BCKL);                // BCKL ON
    gpio_set_direction(ST7789_BCKL, GPIO_MODE_OUTPUT);//
    gpio_set_level(ST7789_BCKL, 1);                   //
    //Shutdowm MAX30102 after boot
    max30102_set_mode(&max30102, MAX30102_SHDN_ON);
    // /*************************************** USER Tick ********************************************/
    // const esp_timer_create_args_t periodic_sec_timer_args = {
    //     .callback = &sec_tick_task,
    //     .name = "sec_tick"
    // };
    // ESP_ERROR_CHECK(esp_timer_create(&periodic_sec_timer_args, &periodic_sec_timer));
    // ESP_ERROR_CHECK(esp_timer_start_periodic(periodic_sec_timer, 1000 * 1000));//定时器单位us，此操作1s调用一次

    // const esp_timer_create_args_t periodic_Xms_timer_args = {
    // .callback = &Xms_tick_task,
    // .name = "Xms_tick"
    // };
    // ESP_ERROR_CHECK(esp_timer_create(&periodic_Xms_timer_args, &periodic_Xms_timer));
    // ESP_ERROR_CHECK(esp_timer_start_periodic(periodic_Xms_timer, 50 * 1000));//定时器单位us，此操作50ms调用一次
    
    lv_task_t * sec_task = lv_task_create(lv_sec_task, 1000, LV_TASK_PRIO_MID,NULL);
    lv_task_t * xms_task = lv_task_create(lv_xms_task, 10, LV_TASK_PRIO_LOW,NULL);
    
    if(ret != 0){
        static const char * notify_btns[] ={"Close", ""};
        guider_ui.notify_msgbox = lv_msgbox_create(lv_scr_act(), NULL);
        lv_msgbox_set_text(guider_ui.notify_msgbox, "Init Error, pls reboot!");
        lv_msgbox_add_btns(guider_ui.notify_msgbox, notify_btns);
        lv_obj_set_width(guider_ui.notify_msgbox, 200);
        lv_obj_align(guider_ui.notify_msgbox, NULL, LV_ALIGN_CENTER, 0, 0);
    }

    while (1) {
        /* Delay 1 tick (assumes FreeRTOS tick is 10ms */
        vTaskDelay(pdMS_TO_TICKS(10));

        /* Try to take the semaphore, call lvgl related function on success */
        if (pdTRUE == xSemaphoreTake(xGuiSemaphore, portMAX_DELAY)) {
            lv_task_handler();
            xSemaphoreGive(xGuiSemaphore);
        }
        /* ------------------- SCR Sleep code ---------------- */
        if ((sleep_flag==0) && (lv_disp_get_inactive_time(NULL) > 30*1000)){
            gpio_pad_select_gpio(ST7789_BCKL);                // BCKL OFF
            gpio_set_direction(ST7789_BCKL, GPIO_MODE_OUTPUT);//
            gpio_set_level(ST7789_BCKL, 0);                   //
            sleep_flag=1;
        }else if (sleep_flag && (lv_disp_get_inactive_time(NULL) <= 30*1000)){
            gpio_pad_select_gpio(ST7789_BCKL);                // BCKL ON
            gpio_set_direction(ST7789_BCKL, GPIO_MODE_OUTPUT);//
            gpio_set_level(ST7789_BCKL, 1);                   //
            sleep_flag=0;
        }
        if (az > 10000){
            lv_disp_trig_activity(NULL); //when screen up, trigger it to avoid inactive_time over
        }
        /* ------------------- SCR Sleep code ---------------- */
    }

    /* A task should NEVER return */
    free(buf1);
#ifndef CONFIG_LV_TFT_DISPLAY_MONOCHROME
    free(buf2);
#endif
    vTaskDelete(NULL);
}


static void lv_tick_task(void *arg) {
    (void) arg;

    lv_tick_inc(LV_TICK_PERIOD_MS);
}

void lv_sec_task(lv_task_t * sec_task){
    if(time_sec<59){
        time_sec++;
    }else{
        time_sec = 0;
        if(time_min<59){
            time_min++;
        }else{
            time_min=0;
            if(time_hour<23){
                time_hour++;
            }else{time_hour=0;}
        }
        if((lv_scr_act() == guider_ui.Timehome) && scrloading==0){
            Timeset_func(&guider_ui,time_hour,time_min,time_day);//display update every min
        }
    }
    if(time_sync_flag && (lv_scr_act() == guider_ui.Timehome) && scrloading==0)//sync time now
    {
        Timeset_func(&guider_ui,time_hour,time_min,time_day);
        time_sync_flag=0;
    }
    if(scrloading==0){
        //tempset
        temp_value = (float)GetTemperature();
        if(temp_value > 30.9)
        {
            people_flag=1;
        }else people_flag=0;  
        Tempset_func(&guider_ui,temp_value);
        //stepset
        // dmp_get_pedometer_step_count(&step_count);
        Stepset_func(&guider_ui,step_count,stepDis);
        //HRset
        HR_func(&guider_ui,result.heart_bpm,result.spO2);
        //memory_print();
    }
    if (time_min%5==0 && time_sec==0){
        max30102_set_mode(&max30102, MAX30102_SHDN_OFF);//start max30102
        HR_TIM_CNT=0;
    }
}
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

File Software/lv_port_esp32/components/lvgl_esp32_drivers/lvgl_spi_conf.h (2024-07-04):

/**
 * @file lvgl_spi_conf.h
 *
 */

#ifndef LVGL_SPI_CONF_H
#define LVGL_SPI_CONF_H

#ifdef __cplusplus
extern "C" {
#endif

/*********************
 *      INCLUDES
 *********************/

/*********************
 *      DEFINES
 *********************/
// DISPLAY PINS
#define DISP_SPI_MOSI CONFIG_LV_DISP_SPI_MOSI
#if defined (CONFIG_LV_DISPLAY_USE_SPI_MISO)
    #define DISP_SPI_MISO CONFIG_LV_DISP_SPI_MISO
    #define DISP_SPI_INPUT_DELAY_NS CONFIG_LV_DISP_SPI_INPUT_DELAY_NS
#else
    #define DISP_SPI_MISO (-1)
    #define DISP_SPI_INPUT_DELAY_NS (0)
#endif
#if defined(CONFIG_LV_DISP_SPI_IO2)
#define DISP_SPI_IO2 CONFIG_LV_DISP_SPI_IO2
#else
#define DISP_SPI_IO2 (-1)
#endif
#if defined(CONFIG_LV_DISP_SPI_IO3)
#define DISP_SPI_IO3 CONFIG_LV_DISP_SPI_IO3
#else
#define DISP_SPI_IO3 (-1)
#endif
#define DISP_SPI_CLK CONFIG_LV_DISP_SPI_CLK
#if defined (CONFIG_LV_DISPLAY_USE_SPI_CS)
    #define DISP_SPI_CS CONFIG_LV_DISP_SPI_CS
#else
    #define DISP_SPI_CS (-1)
#endif

/* Define TOUCHPAD PINS when selecting a touch controller */
#if !defined (CONFIG_LV_TOUCH_CONTROLLER_NONE)

/* Handle FT81X special case */
#if defined (CONFIG_LV_TFT_DISPLAY_CONTROLLER_FT81X) && \
    defined (CONFIG_LV_TOUCH_CONTROLLER_FT81X)

    #define TP_SPI_MOSI CONFIG_LV_DISP_SPI_MOSI
    #define TP_SPI_MISO CONFIG_LV_DISP_SPI_MISO
    #define TP_SPI_CLK  CONFIG_LV_DISP_SPI_CLK
    #define TP_SPI_CS   CONFIG_LV_DISP_SPI_CS
#else
    #define TP_SPI_MOSI CONFIG_LV_TOUCH_SPI_MOSI
    #define TP_SPI_MISO CONFIG_LV_TOUCH_SPI_MISO
    #define TP_SPI_CLK  CONFIG_LV_TOUCH_SPI_CLK
    #define TP_SPI_CS   CONFIG_LV_TOUCH_SPI_CS
#endif
#endif

#define ENABLE_TOUCH_INPUT  CONFIG_LV_ENABLE_TOUCH

#if defined (CONFIG_LV_TFT_DISPLAY_SPI_HSPI)
    #if CONFIG_IDF_TARGET_ESP32C3
        #define TFT_SPI_HOST SPI2_HOST
    #else
        #define TFT_SPI_HOST HSPI_HOST
    #endif
#elif defined (CONFIG_LV_TFT_DISPLAY_SPI_VSPI)
#define TFT_SPI_HOST VSPI_HOST
#elif defined (CONFIG_LV_TFT_DISPLAY_SPI_FSPI)
#define TFT_SPI_HOST FSPI_HOST
#endif

#if defined (CONFIG_LV_TFT_DISPLAY_SPI_HALF_DUPLEX)
#define DISP_SPI_HALF_DUPLEX
#else
#define DISP_SPI_FULL_DUPLEX
#endif

#if defined (CONFIG_LV_TFT_DISPLAY_SPI_TRANS_MODE_DIO)
#define DISP_SPI_TRANS_MODE_DIO
#elif defined (CONFIG_LV_TFT_DISPLAY_SPI_TRANS_MODE_QIO)
#define DISP_SPI_TRANS_MODE_QIO
#else
#define DISP_SPI_TRANS_MODE_SIO
#endif

#if defined (CONFIG_LV_TOUCH_CONTROLLER_SPI_HSPI)
#define TOUCH_SPI_HOST HSPI_HOST
#elif defined (CONFIG_LV_TOUCH_CONTROLLER_SPI_VSPI)
#define TOUCH_SPI_HOST VSPI_HOST
#elif defined (CONFIG_LV_TOUCH_CONTROLLER_SPI_FSPI)
#define TOUCH_SPI_HOST FSPI_HOST
#endif

/* Handle the FT81X Special case */
#if defined (CONFIG_LV_TFT_DISPLAY_CONTROLLER_FT81X)

#if defined (CONFIG_LV_TOUCH_CONTROLLER_FT81X)
#define SHARED_SPI_BUS
#else
/* Empty */
#endif

#else
// Detect the use of a shared SPI Bus and verify the user specified the same SPI bus for both touch and tft
#if defined (CONFIG_LV_TOUCH_DRIVER_PROTOCOL_SPI) && TP_SPI_MOSI == DISP_SPI_MOSI && TP_SPI_CLK == DISP_SPI_CLK
#if TFT_SPI_HOST != TOUCH_SPI_HOST
#error You must specify the same SPI host (HSPI, VSPI or FSPI) for both display and touch driver
#endif

#define SHARED_SPI_BUS
#endif

#endif

/**********************
 *      TYPEDEFS
 **********************/
#if defined (CONFIG_LV_TFT_DISPLAY_CONTROLLER_ILI9481) || \
    defined (CONFIG_LV_TFT_DISPLAY_CONTROLLER_ILI9488)
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
